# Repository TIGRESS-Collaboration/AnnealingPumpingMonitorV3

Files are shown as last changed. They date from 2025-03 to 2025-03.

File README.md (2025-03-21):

# PumpingMoniterV3

This repo contains updated code and documentation for the HPGe pumping station remote loggers in the tiglab.

## Function

The datalogger uses a function called readData.cpp to poll data from the arduino. The polling rate can be changed but is automatically set to 10s. Another function, checkUptime.py, ensures that the data logger continues to run. The data can be viewed on the website in plot and text form. The button functionality is done using php scripts in the action directory. The buttons are all fairly self-explanatory but are outlined clearly in the [previous version repository](https://github.com/TIGRESS-Collaboration/AnnealingPumpingMonitorVer2/blob/master/README.md). A more in depth explanation of the loggers functions can be found here as well.

## Server setup instructions

### Dependencies

There are a few packages that must be installed when setting up a new raspberry pi.

1. rename command
2. gawk
3. screen
4. php-fpm (any version is fine, the most up to date is likely best, but make sure that you update this in the nginx default site configuration)
   
### Other software to download

The setup runs using nginx to host a local server and uses the UUGear library to interface with the arduino. The code contains the necessary parts of the UUGear library on the raspberry pi side, however [this sketch](https://github.com/uugear/UUGear/blob/master/Arduino/UUGear/UUGear.ino) must be uploaded to the arduino.

### Installation steps

1. Setup the raspberry pi. The default operating system and settings should be sufficient. Set the username to tigress.
2. In the tigress home directory install the zip file from this repository. Unzip the file and rename the directory to 'site'.
3. Install nginx into the etc directory. When installed, the localhost page should show a basic nginx welcome message.
4. Go to the sites-available directory and edit the default file. After this is done the local host page should show the site, but with little functionality.
  - Open the default file in the following directory:
     
```
cd etc/nginx/sites-available/
```
  - Change the root from the default to:
```
/home/tigress/site/www
```
  - Add index.php to a list, the default file should have a comment flagging when to do so
  - Uncomment a few lines of code enabling fastcgi with php-fpm (This is where you must input the correct php version that you have downloaded).
  - Change the access and error log paths from the default (In the current setup they are in the directory /home/tigress/site/logs). For the error log, set the warn level to error. This means adding the word error after the file path.
```
error_log /home/tigress/site/logs/error.log error;
access_log /home/tigress/site/logs/access.log;
```
5. Setup files and paths   
  - Create the backupLogs directory within the datalogs directory. www-data should do this:
```
cd home/tigress/site/www/datalogs/
sudo -u www-data mkdir backupLogs
```
  - Create shared json files in /home/sharedjson/jsonFiles and, ensure that www-data can read and write to these files
    - calibTime.json
    - config.json
    - ionConst.json
    - plotConfig.json
    - samplerate.json
    - tcConst.json
    - tempConst.json
   
  - Create datalogs.csv in the datalogs directory

6. Set up the arduino
   - Upload the [this sketch](https://github.com/uugear/UUGear/blob/master/Arduino/UUGear/UUGear.ino) to the arduino.
   - After connecting the arduino, navigate to the site bin directory and use the command ./lsuu to find the arduino serial number. Add this number into the readData.cpp source code.

7. Compile code and start running
   - Submit calibration files by clicking edit settings in the top right corner of the site. Submit calibrations to each of the recalibrate pages. This updates the associated json files. Without this, readData will fail at runtime as it will not be able to parse the json files.
   - buildcpp.sh is a script to recompile readData.cpp. This should be run prior to running the monitor for the first time.
   - startMonitor.sh is the script that starts checkUptime.py which in turn starts readData.cpp. Running this *should* start the logger. If the monitor has started properly, the command screen -ls should show pyscript and readData sessions.

8. Change the device node name and enable ssh
   - To run the raspberry pi as a headless device you must enable ssh. This may already be done. If not, ensure that you have generated hostkeys and that access is restricted such that only root can read and write (not execute). Also make sure that hostkeys have been uncommented in the ssh configuration files. This can all be found in the directory /etc/ssh/.
   - The device will likely have to be added to TRIUMF's iot. They will change the node name in accordance with our request.

## Troubleshooting

To confirm that the logger is running use the command ps -aux in the terminal. You should see processes running for both readData and checkUptime. readData or both readData and checkUptime are not there, you can try starting readData from the bin directory using the command ./readDatacpp. If the error message gives warnings about UUGear, you can try resetting the arduino and unplugging it and plugging it back in. If the problem persists, consider reuploading the UUGear sketch to the arduino.

If readData still refuses to start, ensure that the sharedJson files that were created in step 5 of setup are populated with the values you submitted to the website. It may also be worth checking that the directory structure is set up correctly, and that the functions are not trying to access any directories or files that don't exist.

If the functions are running but there are issues with site functionality, check the error log in the logs directory. Here, errors that have to do with the site functionality will be logged. 

If there seems to be some other issue, you can try viewing the functions of readData and checkUptime by viewing their screen sessions. The command screen -ls will show all current screen sessions. If readData or checkUptime is here, you should be able to view the session with screen -r readData or screen -r checkUptime.

It may also be worth looking at the two previous repositories [Version 1](https://github.com/TIGRESS-Collaboration/AnnealingPumpingMonitor), [Version 2](https://github.com/TIGRESS-Collaboration/AnnealingPumpingMonitorVer2/blob/master/README.md) to see if there are any hints there.

## Physical setup instructions

The logger has three physical parts, the arduino, the raspberry pi, and a custom PCB. At some point in the past, many of the PCB were ordered and at the time of the setup of grspi03, there are 6 still unsoldered in a bin somewhere. The components required likely *aren't* in a bin somewhere, but if you are soldering a new one, you will need the following components:

The arduino must be connected via USB to the raspberry pi, and the raspberry pi must be plugged into a power source. Keep this in mind when choosing and setting up the enclosure for the logger. Currently, grspi03 is using [this enclosure](https://www.digikey.ca/en/products/detail/hammond-manufacturing/1598CSGY/153164), although if you use this one you will need to get new end pieces made out of insulating material or get insulated BNC feed-throughs for the inputs, as in principle the temperature inputs are meant to have a different ground than the pressure inputs. This being said, this enclosure is approaching the minimum size that would fit all of the necessary components. In this enclosure, we have set up the arduino and raspberry pi to use 1 inch standoffs, and the PCB to use 1/4 inch standoffs, so that the arduino to raspberry pi cable can run over the PCB.

The arduino must be wired in the following way:

1. 3.3V power socket to the AREF digital socket
2. RTD1 PCB output to A2 analog input
3. RTD2 PCB output to A3 analog input
4. IG PCB output to A5 analog input
5. TC2 PCB output to A4 analog input
6. PCB ground screw terminal to GND power socket
7. PCB 5V screw terminal to 5V power socket
8. USB cable from arduino to raspberry pi

The PCB input mapping is clearly labeled on the PCB and should not require much further explanation.

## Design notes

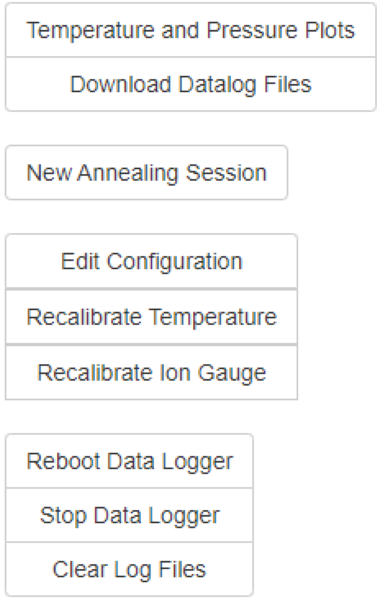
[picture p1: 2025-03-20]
buttons.png

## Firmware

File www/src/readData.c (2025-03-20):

#include <stdlib.h>
#include <stdio.h>
#include <string.h>
#include <sys/stat.h>
#include <sys/types.h>
#include <mqueue.h>
#include <unistd.h>
#include <time.h>
#include <math.h>

#include "srcUUGear/UUGear.h"

//Define constants

#define EXTERNAL 1		// For external ADC reference voltage
#define INTERNAL 0		// For Vcc to be the ADC reference voltage
#define ADC_RES 1023	// ADC resolution
#define GAIN_IG 3.29
#define GAIN_TC2 3.33
#define SAMPLE_NUM 100
#define PAST_NUM 15
#define PIN_NUM 4


#define IG_ALGORITHM 11 // For the Ion-Gauge pressure conversion
#define TC_ALGORITHM 4  // For the thermocouple pressure conversion

#ifndef TEMP_CONV_1
	#define TEMP_CONV_1 146.8331143
#endif

#ifndef TEMP_OFFSET_1
	#define TEMP_OFFSET_1 -260.9097503
#endif

#ifndef TEMP_CONV_2
    #define TEMP_CONV_2 132.7957508
#endif

#ifndef TEMP_OFFSET_2
    #define TEMP_OFFSET_2 -234.2247224
#endif

#ifndef PT100_IN1 		// Define the input pins
	#define PT100_IN1 2
#endif 

#ifndef PT100_IN2
	#define PT100_IN2 3
#endif

#ifndef IG_IN
	#define IG_IN 5
#endif

#ifndef TC2_IN
	#define TC2_IN 4
#endif

#ifndef CAL_PT100 		// These are FINAL READING calibrations (ie. in Volts, degree Celsius, Torr, etc...)
	#define CAL_PT100 0.0
#endif

#ifndef CAL_IG
    #define CAL_IG -0.1 // This is likely to change later
#endif

#ifndef CAL_TC2
    #define CAL_TC2 -0.00 // This is likely to change later
#endif

#ifndef CAL_5V
	#define CAL_5V 3.325
#endif

// Just some conversion functions for temperature and pressure
// double cal is the calibration offset between the measurement from the detector lab boxes to the calculated value here
float volt2Pressure(double voltage, int expFactor, float gain, double cal) {
	int exp;
	float pressure;

	voltage = (voltage + cal)* gain;
	exp = (int)floor(voltage) - expFactor;

	// Decode the mantissa
	if (exp < 0) 
		pressure = ((voltage - floor(voltage) + 0.1) / 0.11)/pow(10,-1*exp);
	else
		pressure = ((voltage - floor(voltage) + 0.1) / 0.11)*pow(10,exp);
	 
	return pressure;
}

float volt2Temperature(float voltage, float conv, float offset, double cal) {
    double temp;

	temp = (double) ((voltage+cal) * conv + offset); // Simple linear relation

    return temp;
}

// Simple moving average filter 
float filterSMA(int newData[PIN_NUM], int oldData[PAST_NUM * PIN_NUM], float average[PIN_NUM]) {
	int ii, jj;
	int sum[PIN_NUM];

	// First shift all old values back in old array
	for (ii = 0; ii < PIN_NUM; ii++) {
		sum[ii] = 0;
		for (jj = ii * PAST_NUM; jj < PAST_NUM * (ii + 1); jj++) {
			if (jj == PAST_NUM * (ii + 1) - 1) {
				oldData[jj] = newData[ii];
			} else {
				oldData[jj] = oldData[jj + 1];
			}
			sum[ii] += oldData[jj]; // Then add the new value to the current sum.
		}			
		average[ii] = (float) sum[ii] / PAST_NUM; // Take the average
	}
}

// This is the overall noise filter. It has 3 steps:
// 1) Take a sample set of data. Order them
// 2) Take the mean of the median values in the ordered set
// 3) Thilter this value further by taking the simple moving average with previous measured values
float readADCNoiseFilter(UUGearDevice dev, int pin[PIN_NUM], float readings[PIN_NUM], int oldData[PIN_NUM * PAST_NUM]) {
	int sample[PIN_NUM * SAMPLE_NUM];
	int sum[PIN_NUM];
	float sumSMA[PIN_NUM];
	int swap = 0;
	int ii, jj;

	for (ii = 0; ii < PIN_NUM; ii++) {
		for (jj = ii * SAMPLE_NUM; jj < SAMPLE_NUM * (ii + 1); jj++) {
			sample[jj] = analogRead(&dev, pin[ii]);
			//usleep(500);
			//printf("Reading: %d from pin %d\n", sample[jj], pin[ii]);
		}
	}

    for (ii = 0; ii < PIN_NUM; ii++) {
        for (jj = ii * SAMPLE_NUM; jj < SAMPLE_NUM * (ii + 1); jj++) {
			if (sample[jj] > sample [jj + 1]) {
				swap = sample[jj];
				sample[jj] = sample[jj + 1];
	            sample[jj + 1] = swap;
			}
        }
    }

    for (ii = 0; ii < PIN_NUM; ii++) {
        sum[ii] = 0;
    }

    for (ii = 0; ii < PIN_NUM; ii++) {
        for (jj = 0; jj < 50; jj++) {
            sum[ii] += sample[ii*SAMPLE_NUM+25+jj];
        }
    }

	filterSMA(sum, oldData, sumSMA);

	for (ii = 0; ii < PIN_NUM; ii++) {
		readings[ii] = sumSMA[ii] / 50;
	}
}

int main(int argc, char **argv)
{
    setupUUGear();
    setShowLogs(1);
    UUGearDevice dev = attachUUGearDevice ("UUGear-Arduino-9046-1419");

	analogReference(&dev, EXTERNAL); // set AREF to external (3.3V regulated line, in this case)

    if (dev.fd != -1) {
		int j ; //, sumPT100Box, sumSTIG, sumSTTC2;
		//int senTorrIG = 5;		// analog in pin 5
		//int senTorrTC2 = 4;		// analog in pin 4
        //int pt100Box = 2;    	// analog input pin 2
		int oldADC[PIN_NUM * PAST_NUM];

		for (j = 0; j < PIN_NUM*PAST_NUM; j++) {
			oldADC[j] = 0;
		}

		char strCurrTime[21];
        float voltPT1001, voltPT1002 ;
		double voltSTIG, voltSTTC2;
		float tempPT1001, tempPT1002, presSTIG, presSTTC2;

		int pin[] = {PT100_IN1, PT100_IN2, IG_IN, TC2_IN};
		//int pinNum = sizeof(pin) / sizeof(int);

		float readings[PIN_NUM];

		voltPT1001 = 0; voltSTIG = 0; voltSTTC2 = 0;

		time_t pastTime;
		time(&pastTime);
		struct tm tmPTime;
		tmPTime  = *localtime(&pastTime);

		time_t currTime;
		struct tm tmCurrTime;

		// Initializing files
		FILE *currRead; // This should overwrite old file
		char currReadFN[] = "../../../site/www/datalogs/currentReading.txt";
	    printf("Creating file \"%s\"\n", currReadFN);
   	 	currRead = fopen(currReadFN, "w"); // Overwrite old file
    	if (currRead == NULL) {
        	perror("Failed to create and open file");
        	return EXIT_FAILURE;
    	}
    	fclose(currRead);


		FILE *datalog_timed; // This should simply create a new file
        char datalogTimedFN[56];
        strftime(datalogTimedFN, sizeof(datalogTimedFN), "../../../site/www/datalogs/datalog_%Y%m%d_%H%M%S.txt", &tmPTime);
        printf("Creating file \"%s\"\n", datalogTimedFN);
        datalog_timed = fopen(datalogTimedFN, "a"); // Append to old file (if it exists...)
        if (datalog_timed == NULL) {
            perror("Failed to create and open file");
            return EXIT_FAILURE;
        }
        fclose(datalog_timed);

		FILE *datalog; // This should simply create a new file
		char datalogFN[] = "../datalogs/datalog.txt";
		printf("Opening file \"%s\"\n", datalogFN);
		datalog = fopen(datalogFN, "a"); // Append to old file (if it exists...)
		if (datalog == NULL) {
            perror("Failed to create and open file");
            return EXIT_FAILURE;
        }
        fclose(datalog);
		
		

        while (1 == 1) {
/*
			sumPT100Box = 0;
			sumSTIG = 0;
			sumSTTC2 = 0;

			for (j = 0; j < 200; j++) {
				sumPT100Box += analogRead(&dev, pt100Box);
				sumSTIG += analogRead(&dev, senTorrIG);
				sumSTTC2 += analogRead(&dev, senTorrTC2);
			}

            voltPT100Box = (float)(sumPT100Box * 5 / 200) / 1023;
			voltSTIG = (float) (sumSTIG * 5 / 200) / 1023;
			voltSTTC2 = (float) (sumSTTC2 * 5 / 200) / 1023;
*/

			readADCNoiseFilter(dev, pin, readings, oldADC);

            voltPT1001 = (float)(readings[0] * CAL_5V) / ADC_RES;
			voltPT1002 = (float)(readings[1] * CAL_5V) / ADC_RES;

            voltSTIG = (float) (readings[2] * CAL_5V) / ADC_RES;
            voltSTTC2 = (float) (readings[3] * CAL_5V) / ADC_RES;

			presSTIG = volt2Pressure(voltSTIG, IG_ALGORITHM, GAIN_IG, CAL_IG);
			presSTTC2 = volt2Pressure(voltSTTC2, TC_ALGORITHM, GAIN_TC2, CAL_TC2);
			tempPT1001 = volt2Temperature(voltPT1001, TEMP_CONV_1, TEMP_OFFSET_1, CAL_PT100);
            tempPT1002 = volt2Temperature(voltPT1002, TEMP_CONV_2, TEMP_OFFSET_2, CAL_PT100);

			time(&currTime);
			tmCurrTime  = *localtime(&currTime);

			if(tmCurrTime.tm_mday > tmPTime.tm_mday) {
				strftime(datalogTimedFN, sizeof(datalogTimedFN), "../datalogs/datalog_%Y%m%d_%H%M%S.txt", &tmCurrTime);
        		printf("Creating file \"%s\"\n", datalogTimedFN);
        		datalog_timed = fopen(datalogTimedFN, "a"); // Append to old file (if it exists...)
        		if (datalog_timed == NULL) {
            		perror("Failed to create and open file");
            		return EXIT_FAILURE;
        		}
        		fclose(datalog_timed);
			}

			tmPTime = tmCurrTime;

			strftime(strCurrTime, sizeof(strCurrTime), "%F %H:%M:%S", &tmCurrTime);
			printf("Time: %s    PT100(1): %.1f C    PT100(2): %.1f C    IG: %.2E Torr    TC2: %.2E Torr\n", strCurrTime, tempPT1001, tempPT1002, presSTIG, presSTTC2);

			currRead = fopen(currReadFN, "w");
			fprintf(currRead, "<b>Time:</b> %s <br><b>PT100 (1):</b> %.1f\u2103 &nbsp; %.3fV <br><b>PT100 (2):</b> %.1f\u2103 &nbsp; %.3fV <br><b>IG:</b> %.2E Torr &nbsp; %.3fV<br><b>TC2:</b> %.2E Torr&nbsp; %.3fV", strCurrTime, tempPT1001, voltPT1001, tempPT1002, voltPT1002,  presSTIG, voltSTIG*GAIN_IG,  presSTTC2, voltSTTC2*GAIN_TC2);
			fflush(currRead);
			fsync(fileno(currRead));
			fclose(currRead);
			
			datalog = fopen(datalogFN, "a");
			fprintf(datalog, "%s\t %.1f\t %.3f\t %.1f\t %.3f\t %.2E\t %.3f\t %.2E\t %.3f\n", strCurrTime, tempPT1001, voltPT1001, tempPT1002, voltPT1002, presSTIG, voltSTIG, presSTTC2, voltSTTC2);
			fflush(datalog);
            fsync(fileno(datalog));
			fclose(datalog);

            datalog_timed = fopen(datalogTimedFN, "a");
			fprintf(datalog_timed, "%s\t %.1f\t %.3f\t %.1f\t %.3f\t %.2E\t %.3f\t %.2E\t %.3f\n", strCurrTime, tempPT1001, voltPT1001, tempPT1002, voltPT1002, presSTIG, voltSTIG, presSTTC2, voltSTTC2);
			fflush(datalog_timed);
            fsync(fileno(datalog_timed));
            fclose(datalog_timed);

            //usleep(5000000);
        }
        detachUUGearDevice(&dev);
    }
    else {
        printf("Can not open UUGear device.\n");
    }

    cleanupUUGear();

    return 0;
}

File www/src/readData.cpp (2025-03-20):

#include <stdlib.h>
#include <stdio.h>
#include <string.h>
#include <sys/stat.h>
#include <sys/types.h>
#include <mqueue.h>
#include <unistd.h>
#include <time.h>
#include <math.h>
#include <csignal> //added this
#include <iostream> //added this
#include <fstream>
#include <string>
#include "nlohmann/json.hpp"


extern "C"{
	#include "srcUUGear/UUGear.h"
}

//Define constants

#define EXTERNAL 1	// For external ADC reference voltage
#define INTERNAL 0	// For Vcc to be the ADC reference voltage
#define ADC_RES 1023	// ADC resolution
#define GAIN_IG 3.47
#define GAIN_TC2 3.33
#define SAMPLE_NUM 50
#define MID_NUM 20
#define PAST_NUM 10
#define PIN_NUM 4



#define IG_ALGORITHM 11 // For the Ion-Gauge pressure conversion
#define TC_ALGORITHM 4  // For the thermocouple pressure conversion

//New Consts for new calibration
#define IG_GAIN 0.01063938
#define IG_OFF 0.03272

#ifndef TEMP_CONV_1
	#define TEMP_CONV_1 146.8331143
#endif

#ifndef TEMP_OFFSET_1
	#define TEMP_OFFSET_1 -256.9097503
#endif

#ifndef TEMP_CONV_2
    #define TEMP_CONV_2 132.7957508
#endif

#ifndef TEMP_OFFSET_2
    #define TEMP_OFFSET_2 -231.2247224
#endif

#ifndef PRESS_OFFSET_1
	#define PRESS_OFFSET_1 0.0
#endif

#ifndef PRESS_OFFSET_2
	#define PRESS_OFFSET_2  0
#endif

#ifndef PT100_IN1 		// Define the input pins
	#define PT100_IN1 2
#endif

#ifndef PT100_IN2
	#define PT100_IN2 3
#endif

#ifndef IG_IN
	#define IG_IN 5
#endif

#ifndef TC2_IN
	#define TC2_IN 4
#endif

#ifndef CAL_PT100 		// These are FINAL READING calibrations (ie. in Volts, degree Celsius, Torr, etc...)
	#define CAL_PT100 0.0
#endif

#ifndef CAL_IG
    #define CAL_IG 0.00 // This is likely to change later
#endif

#ifndef CAL_TC2
    #define CAL_TC2 -0.00 // This is likely to change later
#endif

#ifndef CAL_5V
	#define CAL_5V 3.325
#endif

// And any other constants...
const char* UUGEAR_ADDR = "UUGear-Arduino-4274-3768";



/**
 * @brief Converts a voltage to a pressure.
 *        Follows the formula for Ion Gauge conversion in senTorr manual.
 *
 * @param voltage The volatge to be converted.
 * @param expFactor A constant used in the conversion formula (should be 11).
 * @param gain Currently not in use.
 * @param cal Currently not in use.
 * @return The final converted pressure.
 */
float volt2Pressure(double voltage, int expFactor, float gain, double cal) {
	double intpart, decpart;
	int exp;
	float pressure;

	//Gain calibrations done in main()

	//voltage = (voltage + cal) * gain;
	//voltage = voltage * 3.274;
	decpart = modf(voltage, &intpart);
	exp = (int)intpart - expFactor;

	// Decode the mantissa
	if (exp < 0)
		// pressure = ((decpart + 0.1) / 0.11)/pow(10,-1*exp);
		pressure = ((decpart*9.0) + 1.0)/pow(10,-1*exp);
	else
		pressure = ((decpart*9.0)+1.)*pow(10,exp);
	return pressure;
}

/**
 * @brief Converts a given voltage to a temperature. The conversion is a
 *        linear relationship.
 *
 * @param voltage The voltage to be converted.
 * @param conv A conversion constant that represents the slope of the
 * 			   temperature versus votltage plot used for calibration.
 * @param offset A conversion constant that repsresents the y-int of the
 *               same temperature versus voltage plot described above.
 * @param cal Voltage offset.
 * @return The final converted temperature.
 */
float volt2Temperature(float voltage, float conv, float offset, double cal) {
	double temp;
	temp = (double) ((voltage+cal) * conv + offset); // Simple linear relation
    	return temp;
}


//THIS IS CURRENTLY NOT IN USE
/**
 * @brief Performs a simple moving average filter on input data.
 *
 * @param newData Array with new data to be filtered
 * @param oldData Array containing older set of data
 * @param average The output array containing the average of the data
 * @return float NA
 */
float filterSMA(int newData[PIN_NUM], int oldData[PAST_NUM * PIN_NUM], float average[PIN_NUM]) {
	int ii, jj;
	int sum[PIN_NUM];

	// First shift all old values back in old array
	for (ii = 0; ii < PIN_NUM; ii++) {
		sum[ii] = 0;
		for (jj = ii * PAST_NUM; jj < PAST_NUM * (ii + 1); jj++) {
			if (jj == PAST_NUM * (ii + 1) - 1) {
				oldData[jj] = newData[ii];
			} else {
				oldData[jj] = oldData[jj + 1];
			}
			sum[ii] += oldData[jj]; // Then add the new value to the current sum.
		}
		average[ii] = (float) sum[ii] / PAST_NUM; // Take the average
	}
}
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
